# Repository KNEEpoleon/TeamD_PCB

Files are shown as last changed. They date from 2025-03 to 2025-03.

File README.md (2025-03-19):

# TeamD_PCB

This repository contains the PCB design and control system for the BONEPARTE project's drilling subsystem. The project focuses on the development of a printed circuit board (PCB) and associated control mechanisms to support the drilling operations within the BONEPARTE system.

## Files Included:
- **Fusion_Files**: Containsschematic and board design files for the PCB.
- **Gerber_Files**: Contains Gerber files for PCB manufacturing.
- **Libraries**: Custom libraries used in the PCB design.
- **Schematic**: PDF overview the PCB design.
- **BOM**: Bill of Materials for the PCB.
- **DFM**: Design for Manufacturing document outlining manufacturing requirements.

## Installation and Usage
1. Open the Fusion 360 files to modify the PCB design.
2. Use Gerber files for manufacturing the PCB.
3. Refer to the schematic and BOM for assembly and component selection.

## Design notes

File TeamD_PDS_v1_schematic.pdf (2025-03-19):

# Draft Schematic: Power Distribution PCB

### TeamD: KneePolean

### February 28, 2025

## 1 Introduction

This document proposes a Power Distribution System PCB for our manipulator end effector that houses a DC motor, gearbox, and an LED ring light. The system is designed to operate on mains power and will include voltage regulation, connectors, and safety switches.

## 2 System Overview

### 2.1 Power Source

The system will be powered by a standard AC mains supply (120V AC). A standard AC-to-DC adapter will be used to convert the mains voltage to a lower DC voltage. This adapter will provide a stable intermediate 12V DC voltage that will then be stepped down to 3.7V DC using the converter on the PCB.

### 2.2 Subsystems to be Powered

The following subsystems will be powered:

1. DC Motor:
- Voltage Range: 3.7V DC.
- Continuous Current Draw: 2.4A.
- Peak Current Draw: 4.7A (during high torque or stall conditions).
- Regulation: Required to maintain a stable 3.7V output.
2. LED Ring Light:
- Voltage Range: 3.7V DC.
- Current Draw: 0.3A
- Regulation: Not required since connected in parallel with the motor.

3

We used the Texas Instruments [] calculator with the following inputs

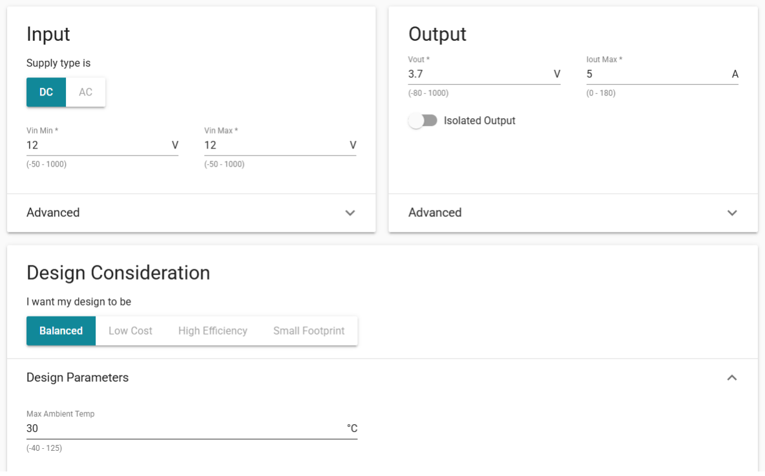
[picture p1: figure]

Figure 1: Enter Caption

To get the basic idea and variations of circuit. Since we found it easiest to integrate the LM2678-ADJ voltage regulator, we decided to go with that for our proejct

## 4 Analysis

1. Voltage Regulator LM2678-ADJ:
- Input Voltage Range: 8V to 40V.
- Output Current: Up to 5A.
- Efficiency: Up to 85-92% under optimal conditions
- Meets the requirement for handling up to 5A for motor operation.
- Adjustable output allows flexibility for tuning motor speed by setting Vout via Rf 1 and Rf 2 .
- High efficiency minimizes power loss, critical for high-current applications.
2. Inductor (L1) 10 µH
- Chosen to handle peak currents without saturation while maintaining low DC resistance.
- Value decided as per below calcualtion

3. Schottky Diode (D1) : 5A Rating
- A low forward voltage drop diode is critical for high efficiency.
- The current rating exceeds the peak inductor current.
4. Input Capacitors (Cin: 82µF, Cnx: 100 nF):
- Filters input ripple; must handle RMS current equal to half the load current.
- Values decided as per TI calculator
5. Output Capacitor (Cout: 330 µF):
- Smooths output voltage; ESR should be low to minimize ripple.
- Values decided as per TI calculator
6. Boost Capacitor (Cb: 10 nF):
- Enhances the performance of the internal switch driver
- Values decided as per TI calculator and datasheet
7. Schottky Diode (D2) : 5A Rating
- To prevent reverse polarity from Vin
8. Fuse : 5A Rating
- To prevent overcurrent from source

### 4.1 L1 Calculation

L =

(Vin − Vout) · D
∆IL · fs

Where:
Vin = 12 V (Input Voltage)

Vout = 3.7 V (Output Voltage)

D =

Vout

Vin

=

3.7
12

= 0.31 (Duty Cycle)

∆IL = 0.2 · Iload = 0.2 · 5 = 1 A (Ripple Current)

fs = 260 kHz = 260 × 10³ Hz (Switching Frequency, from LM2678 datasheet)

Substituting:

L =

(12 − 3.7) · 0.31
1 · 260 × 10³

≈ 10 µH

### 4.2 R Calculation

Vout = Vref ·

1 +

Rf2

Rf1

Where:

Vout = 3.7 V (Output Voltage)
Vref = 1.21 V (Reference Voltage of LM2678) Rf1 = 1 kΩ

Rearranging for Rf2:

Rf2 = Rf1 ·

Vout

Vref

− 1

= 10 kΩ ·
3.7
1.21

− 1

= 2.05 kΩ

## 5 Heat Dissipation

The total heat dissipation in the circuit is the sum of the power losses in the LM2678 regulator, the Schottky diode (D1), and the inductor (L1):

Ptotal = PLM2678 + PD1 + PL1

### 5.1 Heat Dissipation in the LM2678 Regulator

The power dissipated in the LM2678 is due to conduction and switching losses:

PLM2678 = Pcond + Pswitch

(a) Conduction Losses:

Pcond = I

2
load · RDS(on)

Where:

Iload = 5 A (output current)
RDS(on) = 0.15 Ω (from LM2678 datasheet)

Substituting:

Pcond = (5)²
- 0.15 = 3.75W
(b) Switching Losses:

Pswitch =

1
2
- Vin · Iload · ts · fs

Where:

Vin = 12 V (input voltage)
ts = 50 ns (switching time, estimated from datasheet) fs = 260 kHz = 260 × 10³ Hz (switching frequency)

Substituting:

Pswitch =

1
2
- 12 · 5 · 50 × 10⁻⁹
- 260 × 10³ = 0.39W

Thus, total power dissipated by the LM2678:

PLM2678 = Pcond + Pswitch = 3.75 + 0.39 = 4.14W

### 5.2 Heat Dissipation in Schottky Diode (D1)

The power dissipated in D1 is due to its forward voltage drop:

PD1 = ID · Vf

Where:

ID = Iload = 5 A (current through diode)
Vf = 0.5 V (forward voltage drop of typical Schottky diode)

Substituting:
PD1 = 5 · 0.5 = 2.5W

### 5.3 Heat Dissipation in Inductor (L1)

The power dissipated in L1 is due to its DC resistance (RL):

PL1 = I

2
load · RL

Where:
RL = 0.05 Ω (typical DC resistance for a low-DCR inductor)

Iload = 5 A

Substituting:
PL = (5)²
- 0.05 = 1.25 W

### 5.4 Thermal Management

Although the heat produced here is minimal, the maximum current conditions could be high. For safety reasons, the overall container housing this PCB will be made to maintain good air flow, and a simple heatsink will be added on top of the LM2678.

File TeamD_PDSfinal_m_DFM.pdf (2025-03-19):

## TEAM D: KNEEPolean Power Distribution System: DFM Report

Multilayer PDF output resultshttps://www.freedfm.com/freedfm/0038180006222858/FreeDFM-v2.0/freeDFM.pdf Plotshttps://www.freedfm.com/freedfm/0038180006222858/results/plots.htm
DFM Resultshttps://www.freedfm.com/freedfm/0038180006222858/results/summary2.htm

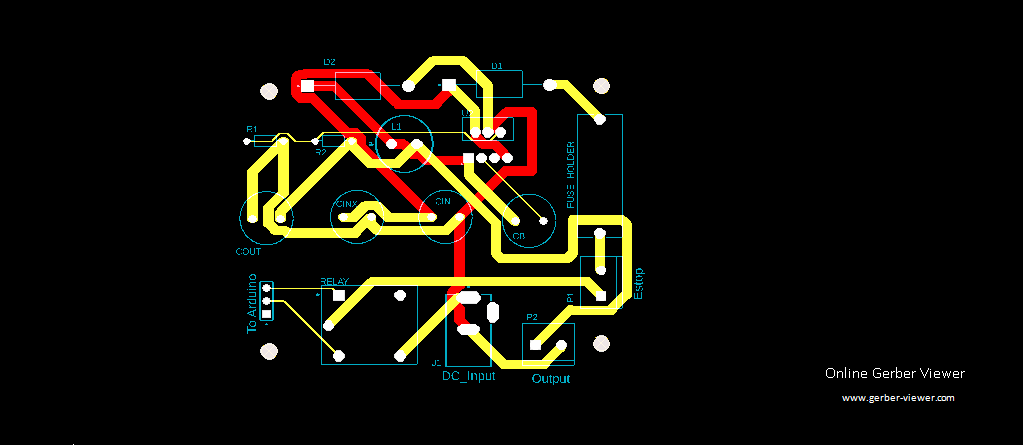
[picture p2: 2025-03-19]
TeamD_PDSfinal_m.png

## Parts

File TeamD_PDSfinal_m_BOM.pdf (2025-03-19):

Item No. | Part Name | Quantity | Value | Part Designator | Manufacturer Part Number | Vendor | Unit Price (USD)
1 PCB Power Relay | | 4 Relay, 5V, 10A | | K1 | SRD-05VDC-SL-C | Amazon | $4.79
2 DC Supply Connector | | 2 20V, 5A | | J1 | DCJ200-10-A-K1-K | DigiKey | $0.720
3 Fuse Holder | | 2 - | | CP1 | 4628 | DigiKey | $0.81
4 Schottky Diode | | 8 100v, 5A | | D1 | SR510 A0G | DigiKey | $0.29
5 Capacitor | | 4 0.1uF, 50V | | C1 | C317C104M5U5TA7317 | DigiKey | $0.34
6 Capacitor | | 4 10nF, 25V | | C2 | C322C103K3G5TA | DigiKey | $0.54
7 Capacitor | | 4 82uF, 35V | | C3 | ESW826M035AE4AA | Mouser | $0.44
8 Buck Converter | | 3 40V, 5A | | U1 | LM2678T-ADJ | DigiKey | $7.93
9 Capacitor | | 4 330uF, 25V | | C4 | MAL217056331E3 | Mouser | $1.60
10 Resistor | | 4 2.05K Ohm | | R2 | MFR-25FRF52-2K05 | DigiKey | $0.10
11 Resistor | | 4 1K Ohm | | R3 | CFR-25JB-52-1K | DigiKey | $0.10
12 Emergency Stop | | 2 - | | SW1 | A01ESDM | DigiKey | $13.44
13 2-pin Connector | | 4 300V, 13.5A | | J2 | 282837-2 | DigiKey | $0.90
14 Inductor | | 4 100uH, 5.1A | | L1 | 7447471100 | DigiKey | $2.36
15 Fuse | | 6 6A | | F1 | 0234006.MXP | DigiKey | $1.19
Item No. | Part Name | Quantity | Value | Part Designator | Manufacturer Part Number | Vendor | Unit Price (USD)
1 Cable Sleeve | | 1 Cable Sleeve | | - | 704256852238 | Amazon | $15.99
2 Standoff Kit | | 1 Standoffs | | H1 | - | Amazon | $14.98
3 Heat Sink | | 2 - | | - | 577202B00000G | DigiKey | $0.84
4 AC-DC Adaptor | | 2 12V, 5A | | - | WO DC12V5A-US | B&H | $29

MRSD Project Course 16681-A Task 7.3 Bill of Materials Team D

Parts not on the Board but necessary:

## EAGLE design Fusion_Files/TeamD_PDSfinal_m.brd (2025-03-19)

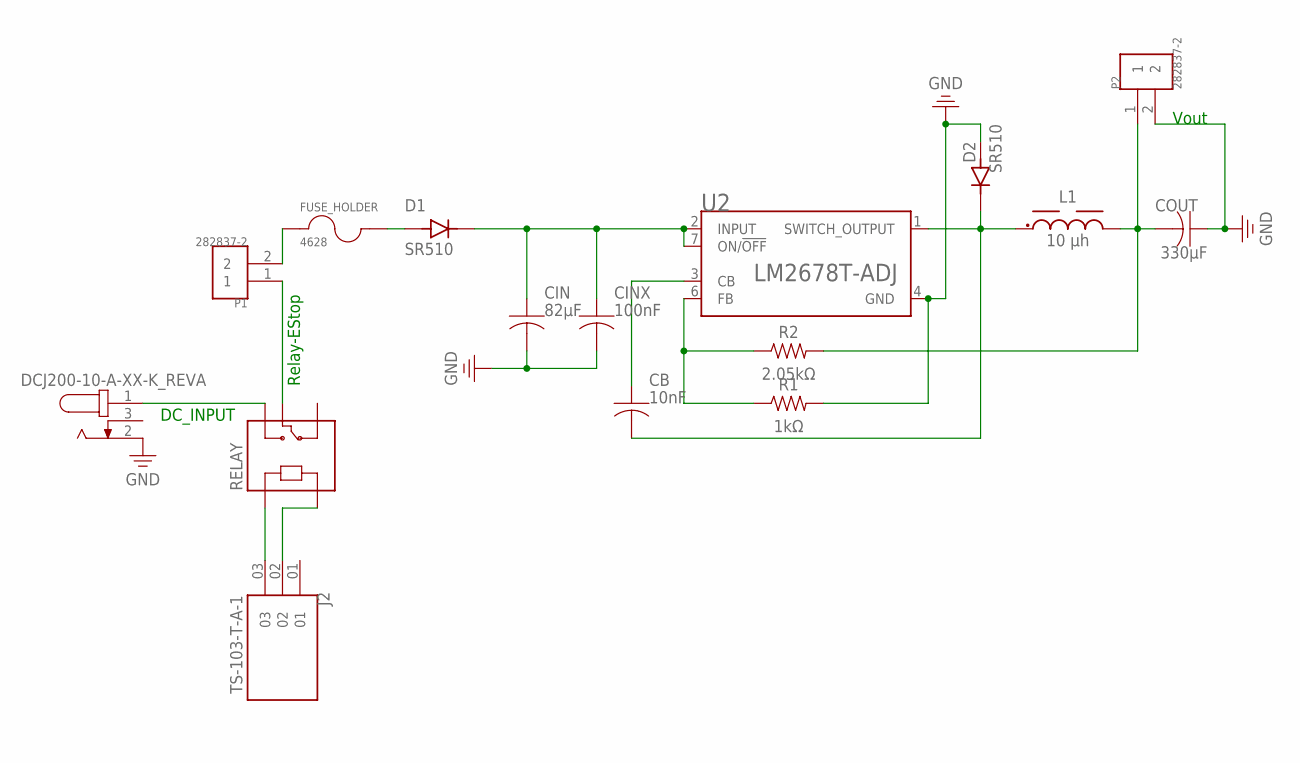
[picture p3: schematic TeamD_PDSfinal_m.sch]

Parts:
CB: 10nF; CAPRD550W60D1025H1250B
CIN: 82μF; CAPRD550W60D1025H1250B
CINX: 100nF; CAPRD550W60D1025H1250B
COUT: 330μF; CAPRD550W60D1025H1250B
D1, D2: SR510; DIOAD1990W125L900D530
FUSE_HOLDER: 4628; FUSE_4628
J1: DCJ200-10-A-XX-K_REVA; GCT_DCJ200-10-A-XX-K_REVA
J2: TS-103-T-A-1; SAMTEC_TS-103-T-A-1
L1: 10 µh; WE-TIS_1111
P1, P2: 282837-2; TE_282837-2
R1: 1kΩ; RESAD724W46L381D178B
R2: 2.05kΩ; RESAD724W46L381D178B
RELAY: SRD-05VDC-SL-C; RELAY_SRD-05VDC-SL-C
U2: LM2678T-ADJ; TO127P1041X469X2199-7N

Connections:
ARDUINO: J2.02, RELAY.A2
ARDUINO_2: J2.03, RELAY.A1
D1_LM2678: CIN.1, CINX.1, D1.C (K), U2.2 (INPUT), U2.7 (ON/!OFF)
DC_RELAY: J1.1, RELAY.NO
ESTOP_FUSE: FUSE_HOLDER.1, P1.2
FUSE_DIODE: D1.A, FUSE_HOLDER.2
GND: CIN.2, CINX.2, COUT.1, D2.A, J1.2, P2.2, R1.2, U2.4 (GND)
IC_CB: CB.1, U2.3 (CB)
IC_R: R1.1, R2.1, U2.6 (FB)
L1_OUT: COUT.2, L1.2, P2.1, R2.2
OUTPUT_L1: CB.2, D2.C (K), L1.1, U2.1 (SWITCH_OUTPUT)
RELAY_ESTOP: P1.1, RELAY.COM

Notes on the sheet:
Vout
DC_INPUT
Relay-EStop

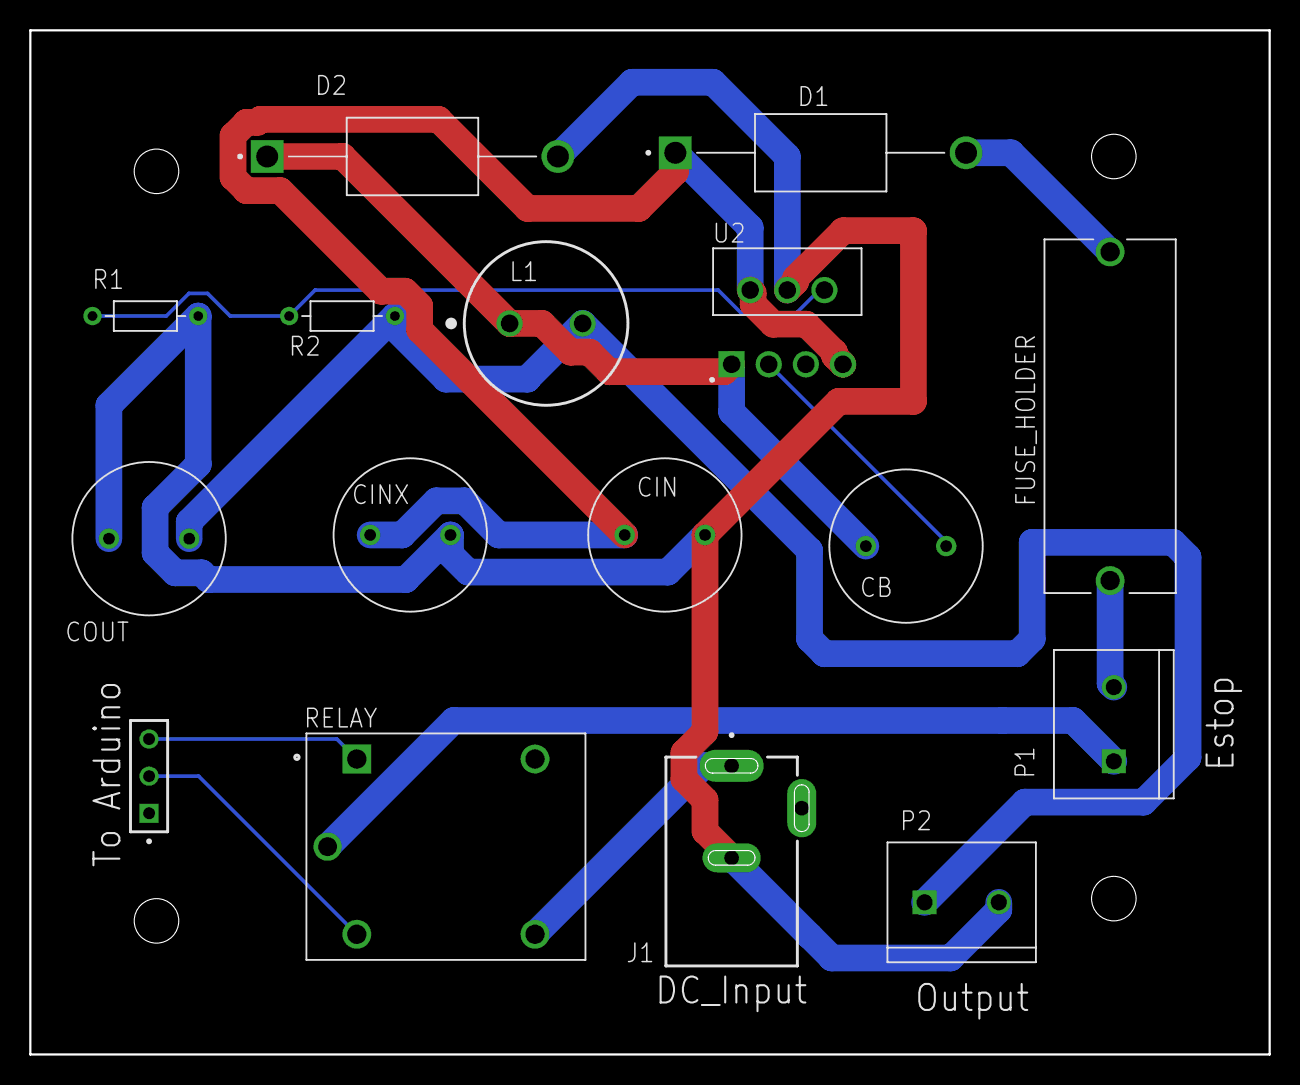
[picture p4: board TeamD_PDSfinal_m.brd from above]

Board: 2 copper layers, 84.8 x 70.1 mm, 16 parts (0 on the bottom side), 12 nets.
